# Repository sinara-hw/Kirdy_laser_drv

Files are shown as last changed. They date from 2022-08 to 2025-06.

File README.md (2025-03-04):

# Kirdy

Low Noise Precision Laser Diode Driver with Built-in TEC Temperature Controller  

## Power Input
| Parameter | Min | Typical | Max | Unit | Condition |
| --- | --- | --- | --- | --- | ---|
| Input Voltage | | 12 | | V | |
| Input Current | | | 2 | A|
| PoE Standard | |  PoE+ (802.3at) | | |

Note: TEC Output Current should be limited to ±2A when it is being powered via PoE(802.3af). Otherwise, Kirdy may malfunction.

## Laser Diode Driver
### Current Source Controller  
| Parameter | Min | Typical | Max | Unit | Condition |
| --- | --- | --- | --- | --- | ---| 
| Resolution | | 0.292 | | uA |
| Control Range| | | 307.2 | mA | |
| Current Limit | | 319. | | mA| |
| Compliance voltage | | > 4.928 | | V | |   
| Current Noise (@ 1 kHz) | | < 300 || pA / rt(Hz) | @ DC Bias: 300 mA, Load: 10 Ω Load|
| RMS Noise(10 Hz - 1 MHz) || < 300 | | nA | @ DC Bias: 300 mA, Load: 10 Ω Load| 
| Temperature Coefficient | | ±1 | | ppm/°C | @ DC Bias: 50 mA. Tested Temperature Range: 43-56 °C |

### Photodiode Input
| Parameter | Min | Typical | Max | Unit | Condition |
| --- | --- | --- | --- | --- | ---|
| Photocurrent Range | 0 | | 3.0 | mA | |
| Photocurrent Resolution | | 0.8 | | uA | |
| Bandwidth (-3 dB) | | 500 | | Hz | |

Note1: Circuit may be damaged if photodiode input current exceeds 3.0 mA. User can modify the circuit and reprogram the photodiode current monitor range via the given driver.

Note2: Photodiode operates in photovoaic mode.

### Low Frequency Modulation Input
| Parameter | Min | Typical | Max | Unit | Condition |
| --- | --- | --- | --- | --- | ---|
| Input Voltage | -1.0 | | 1.0 | V | |
| Input Impedance | | 50 or 43.4k | | ohm | Depends on Termination Switch Position |
| Bandwidth (-3 dB) | | 18 | | MHz | @Modulation Depth: 25 mA/V, Input : 1 Vp-p, DC Bias: 150 mA |

Note: Low Frequency Modulation Input can accept DC input to impose a DC offset to the output current.

## TEC Temperature Controller
### TEC Current Output
| Parameter | Min | Typical | Max | Unit | Condition |
| --- | --- | --- | --- | --- | ---|
| Resolution | | 22.9 | | uA | |
| Control Range (Powered via 12 V Barrel Jack) | -3.0 | | 3.0 | A | With Active Cooling |
| Control Range (Powered via PoE(802.3af)) | -2.0 | | 2.0 | A | |
| Compliance Voltage | | 4.3 |  | V | |
| Voltage Reading Resolution | | 3.22 | | mV | |
| Current Reading Resolution | |  2.0 | | mA | |

### TEC Voltage and Current Limit
| Parameter | Min | Typical | Max | Unit | Condition |
| --- | --- | --- | --- | --- | ---|
| Voltage Limit Settable Range| 0 | | 4.3 | V | |
| Voltage Limit Resolution | | 3.14 | | mV | |
| Current Limit Settable Range | -3.0 | | 3.0 | A | |
| Current Limit Resolution | |  1.57 | | mA | |

### NTC Thermistor Sensor
| Parameter | Min | Typical | Max | Unit | Condition |
| --- | --- | --- | --- | --- | ---|
| Resolution | | 0.01 | | mK | With 10 kohm NTC with 3950 B-Constant, 25°C T0 |
| Sampling Rate | | 16.67 | > 1k | Hz | |

Note: Actual Sampling Rate subjects to device operating conditions.

### Digital PID Temperature Controller
| Parameter | Min | Typical | Max | Unit | Condition |
| --- | --- | --- | --- | --- | ---|
| Temperature Stability | | < 1| | mk | Using supplied Kirdy Adapter with its copper plate installed. PID Parameters are obtained from Kirdy Autotune Algorithm. |

Note: Actual Temperature Stability subjects to the ambient environment conditions.

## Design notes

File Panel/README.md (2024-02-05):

# Kirdy Front Panel 

## Front Panel Text Markings
- Font: PrisonGothicPro-Medium.otf
- Drawn in KiCAD 7

## Front Panel Mechanical Design and Drawings
- Drawn in FreeCAD 0.21.2 with a2plus and Exploded Assembly Workbench installed
- Reference Assembly Kit: nVent SCHROFF 20848-668
- Reference drawings: https://git.m-labs.hk/sinara-hw/front-panels/src/branch/master/Kasli_SOC-vNone

## Front Panel Fiber Optic Adapter Mounting Plates
- Drawn in KiCAD 7
- Mounting Plate can be manufactured as 1.5 mm Aluminum Plate or 1.6 mm Single Layer Aluminum PCB
- Possible Fiber Optic Adapter Compatible for Each Type of Mounting Plate
    - Type 1: SC to SC Fibre Optic Adapter
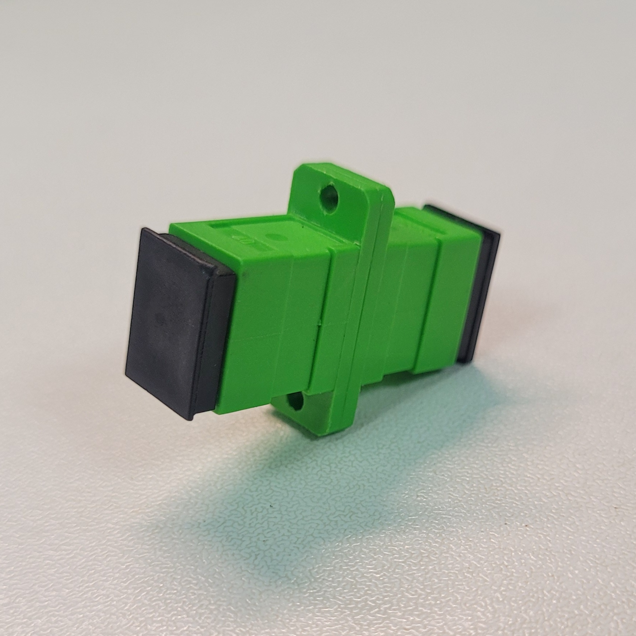
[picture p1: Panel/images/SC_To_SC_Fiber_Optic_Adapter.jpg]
    
    - Type 2: FC to FC Fiber Optic Adapter
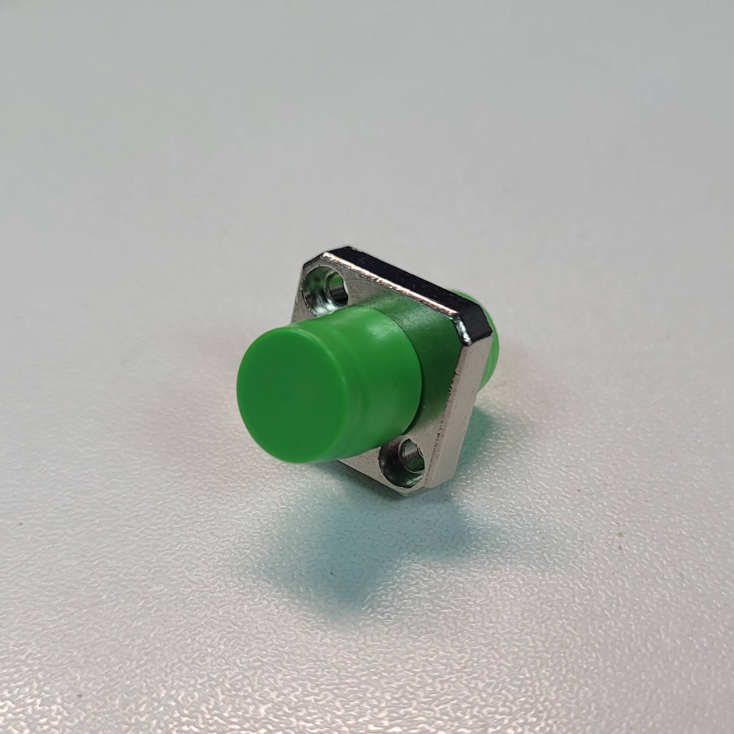
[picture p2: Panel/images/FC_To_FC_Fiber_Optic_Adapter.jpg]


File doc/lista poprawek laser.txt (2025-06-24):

1)add license 0 cerna OHL
2)Add a MOLEX Minifit connector to the board #57
3)Connect 8V LD PWR EN Signal to LD Drive Stage Opamp PD_n
- To all U1, U2, U5 opamp ADA4894-1YRDZ 
4)[Test] Input Power Requirement
- brak reakcji
5) Kirdy HC (High Current) version #54
- brak reakcji 
6) thermoformed plastic laser adapter + fiber holder
- brak reakcji
7)Add Heat Sink to MAX1968 and its Inductors
- 
8) [Test] Evaluation for Maximum Thermostat TEC Output Power
9) generate panel outputs from flake
10) merge flake files
11) 3V3A is unstable if PD Mon Output Stage Voltage is larger than 3.3V
12) move/add protection relay to laser adapter
13) Photodiode Monitor Current Range should be Selectable
14) [TEST] Laser Diode Current Output Temperature Coefficient
15) MAX1968 SHDN Pin is on 5V Voltage Level but it is controlled with 3V3 Voltage Level
16) Mezzanine for second temperature control channel
- nie rozumiem o co im chodzi w tym issiu
17) route relay pins to expansion or laser connector
18) Add a Factory Reset Button for Erasing the settings Stored in Flash
+ rozwiazanie poprzez DFU
19) Add a Switch to the Front Panel for User to Select Whether Kirdy By default Power On Laser Diode and TEC
- nie wiem czy to ma sens
20) Add a 3 Pin Header for Configuring the Photodiode to Operate in Photovoltaic or Photoconductive mode

21) Confusing LD-, LD+, PD- and PD+ Net Name and Markings
- poprawione
22) Lacking EEPROM Preprogrammed with Unique Mac Address
- dodałem pamieci 24AA02E48T-I/OT do STM32 
23) LD overcurrent with all modulation switches are OFF
- nie wiem co z tym zrobic, albo dodac kolejny dzielnik albo moze potencjometr cyfrowy, ale popsuje to szumy
24) Ethernet link drops temporarily when +8V comes on
- faktycznie problem moze istniec, ale autor issiu nie podał powodu i sposobu naprawy
25) PoE unstable power-up
- tu problem jest po stornie switch z POE nie płytki
26) MCU's Firmware Starts before Analog Power Rails are "Power Good"
- dodałem rezystory 10k i linie PG podłaczyłem w wszystkich LDO

wejscie POE/JACK +12V
zaislane z +12V -> 5V
zasilane z +12V -> +3.3V

zasilanie z +12V
+9V 1.5A
+9VA 200mA
+8V
+5VA
zasilane z +5VA  ->   +3.3VA

zasilanie +9V CP
zasilane z -9V   ->   -6V 
+15V

27) Fiber optic adapter mounted on front panel may block the access of alternate programming pin header
+ 28) components bump into card guides
- poprawione, zostały dodane marginesy po 2.5mm z kazdej strony
29) [TEST] LD Driver Current Noise

moje zmiany 
zmiana szerokosci sciezek na 6-8 mil
przelotki zmiana na 0.3/0.6 mm
zmiana layer stack na JLC04161H-3313

- pomiar prądu 
- rozne konfiguracje laser 
+ umascienie katody 
- ba slepo pomiar pradu diody /moc
czy sa kunary ?

TEC - dlaczego niski prad
- ddoac zabzpiecznie na pinach IO
dodać zabezpiczenie do diody laserowej

tylko jeden scalak na BOT !!!!! U3 U6

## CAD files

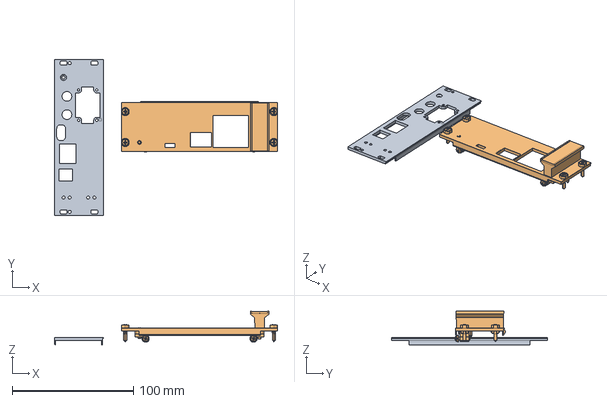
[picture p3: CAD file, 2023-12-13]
Panel/kirdy_front_panel.asm.FCStd
183.7 x 128.4 x 27.8 mm
kirdy_front_panel1_001
Kasli-SOC_Panel1_001

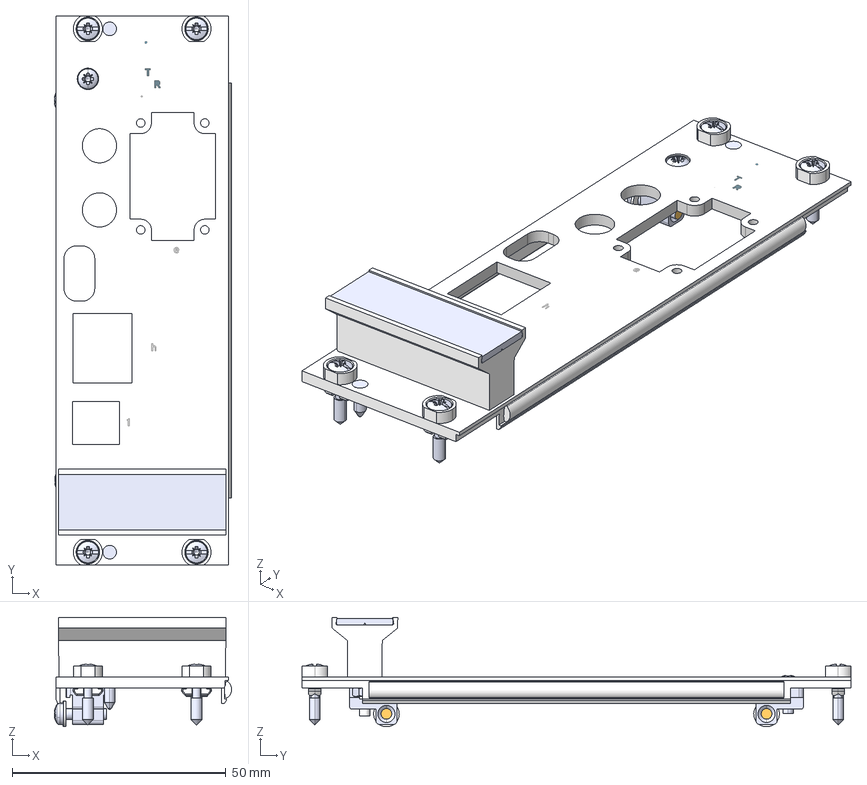
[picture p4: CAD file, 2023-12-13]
Panel/output/FP_1550_3U8HP_PANEL_Mechanical_Drawings_Rev_A/FP_1550_3U8HP_PANEL.step
41.4 x 128.4 x 25.6 mm
FP_1550_3U8HP_CUTOUT_001
SLEEVE GREY PLAS. M2.5 BL
SLEEVE GREY PLAS. M2.5 TL
SLEEVE GREY PLAS. M2.5 TR
SLEEVE GREY PLAS. M2.5 BR
SCREW COLLAR M2.5X12.3 BL
SCREW COLLAR M2.5X12.3 BR
SCREW COLLAR M2.5X12.3 TL
SCREW COLLAR M2.5X12.3 TR
SCR M2.5*8 OVL PHL ST NI
WASHER PLN.M2.7 DIN125 B
SCR M2.5*6 PAN PHL NI DIN7985 B
FP-ALIGNMENT PIN (LOCALIZATION) T
FP-ALIGNMENT PIN (LOCALIZATION) B
EMC GASKET FABRIC 3U

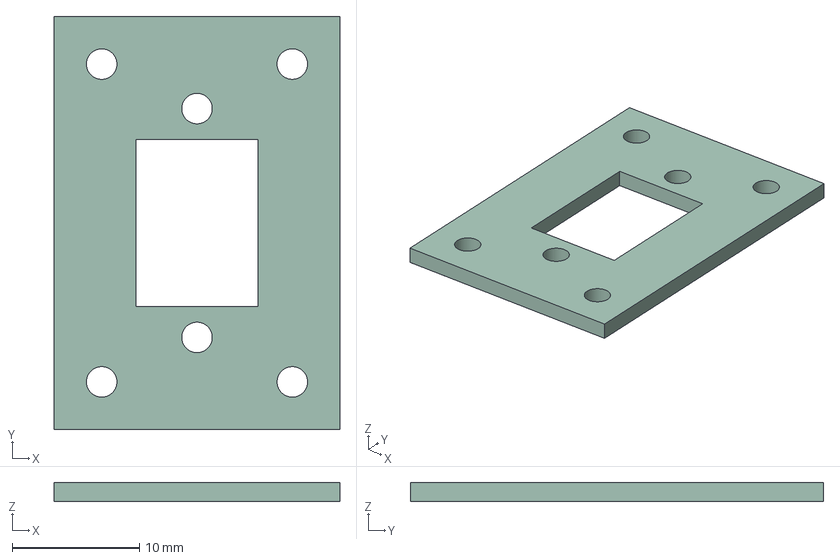
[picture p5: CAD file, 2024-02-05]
Panel/output/FP_1550_Fiber_Optic_Adapter_Mounting_Plate_Type_1/FP_1550_Fiber_Optic_Adapter_Mounting_Plate_Type_1_r0_1rc1.step
22.5 x 32.5 x 1.50 mm

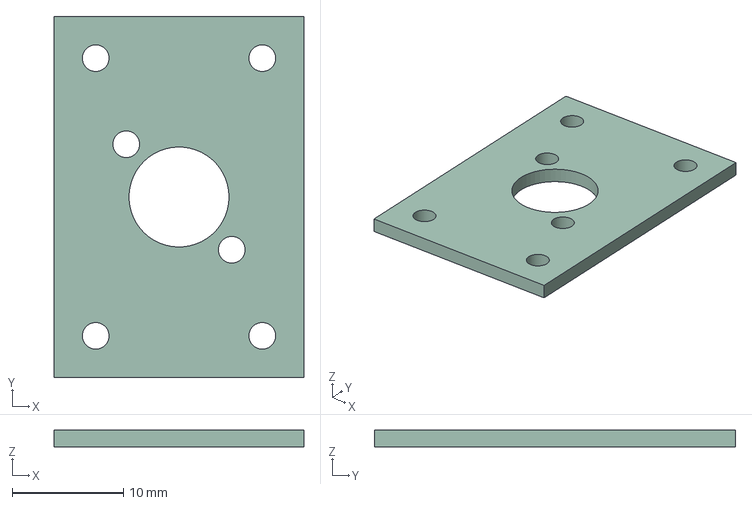
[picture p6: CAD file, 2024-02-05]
Panel/output/FP_1550_Fiber_Optic_Adapter_Mounting_Plate_Type_2/FP_1550_Fiber_Optic_Adapter_Mounting_Plate_Type_2_r0_1rc1.step
22.5 x 32.5 x 1.50 mm

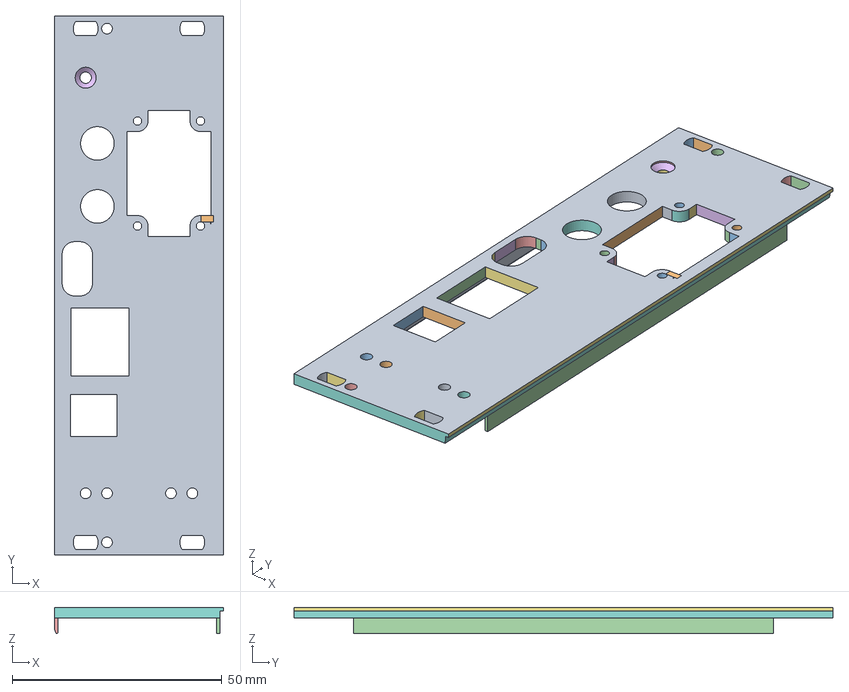
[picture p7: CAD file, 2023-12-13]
Panel/kirdy_front_panel.FCStd
40.3 x 128.4 x 6.20 mm

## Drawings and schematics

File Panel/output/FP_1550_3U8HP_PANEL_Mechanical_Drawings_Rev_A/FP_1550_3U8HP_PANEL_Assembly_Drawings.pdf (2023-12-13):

5 3 4

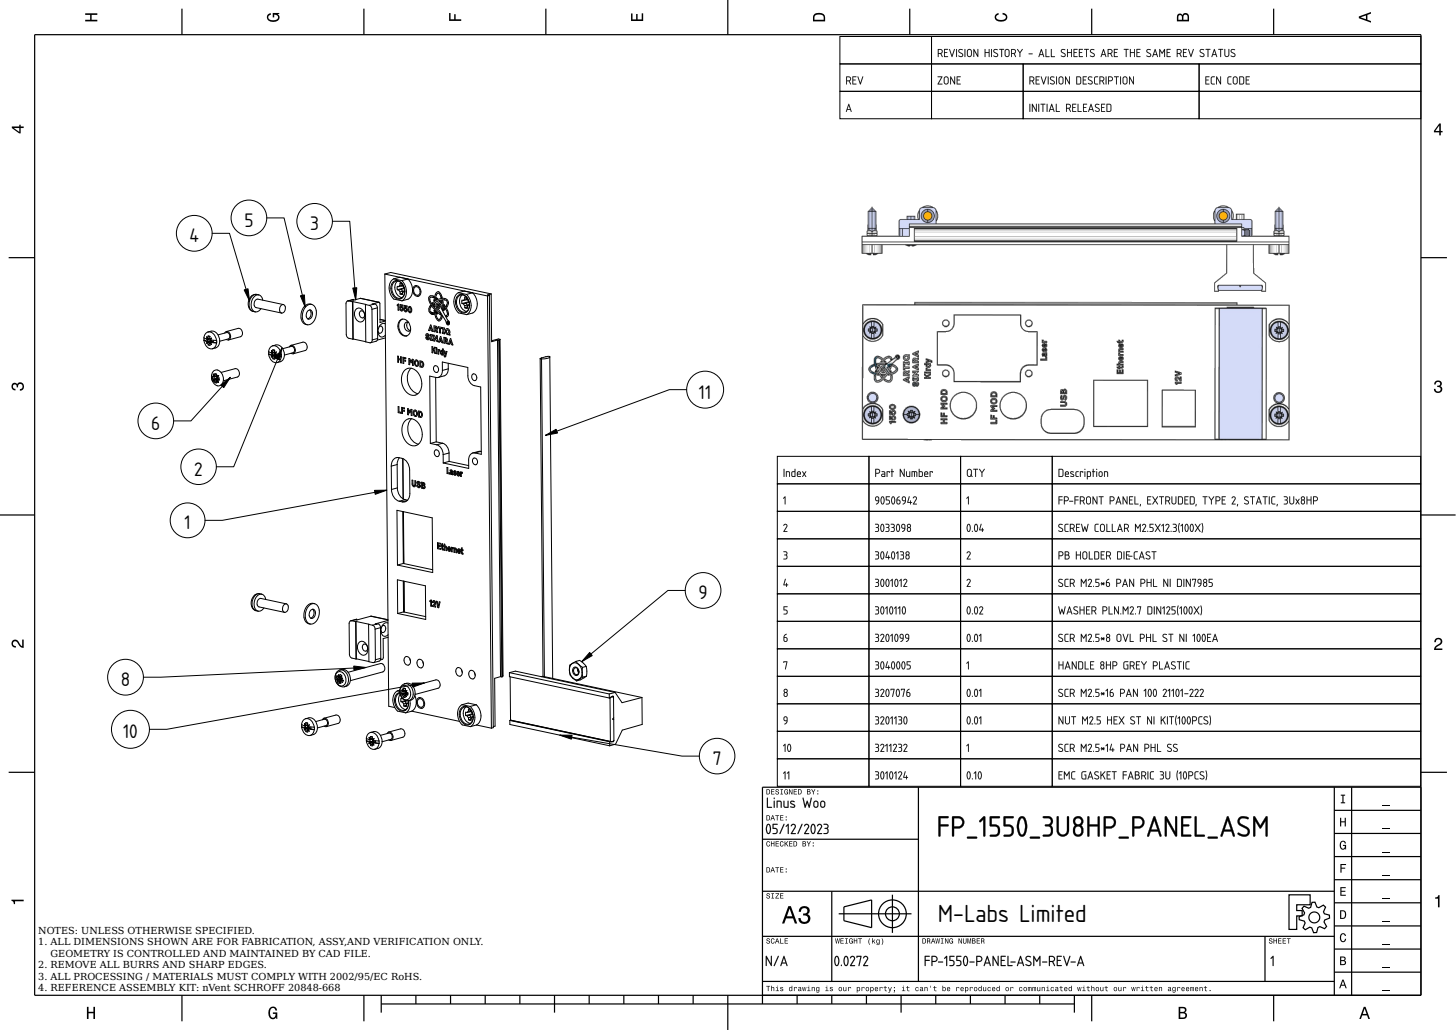
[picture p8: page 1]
M-Labs Limited

NOTES: UNLESS OTHERWISE SPECIFIED. 1. ALL DIMENSIONS SHOWN ARE FOR FABRICATION, ASSY,AND VERIFICATION ONLY. GEOMETRY IS CONTROLLED AND MAINTAINED BY CAD FILE. 2. REMOVE ALL BURRS AND SHARP EDGES. 3. ALL PROCESSING / MATERIALS MUST COMPLY WITH 2002/95/EC RoHS. 4. REFERENCE ASSEMBLY KIT: nVent SCHROFF 20848-668

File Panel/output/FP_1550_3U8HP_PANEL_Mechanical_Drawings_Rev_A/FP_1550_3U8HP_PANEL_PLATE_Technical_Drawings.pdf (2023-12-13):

4

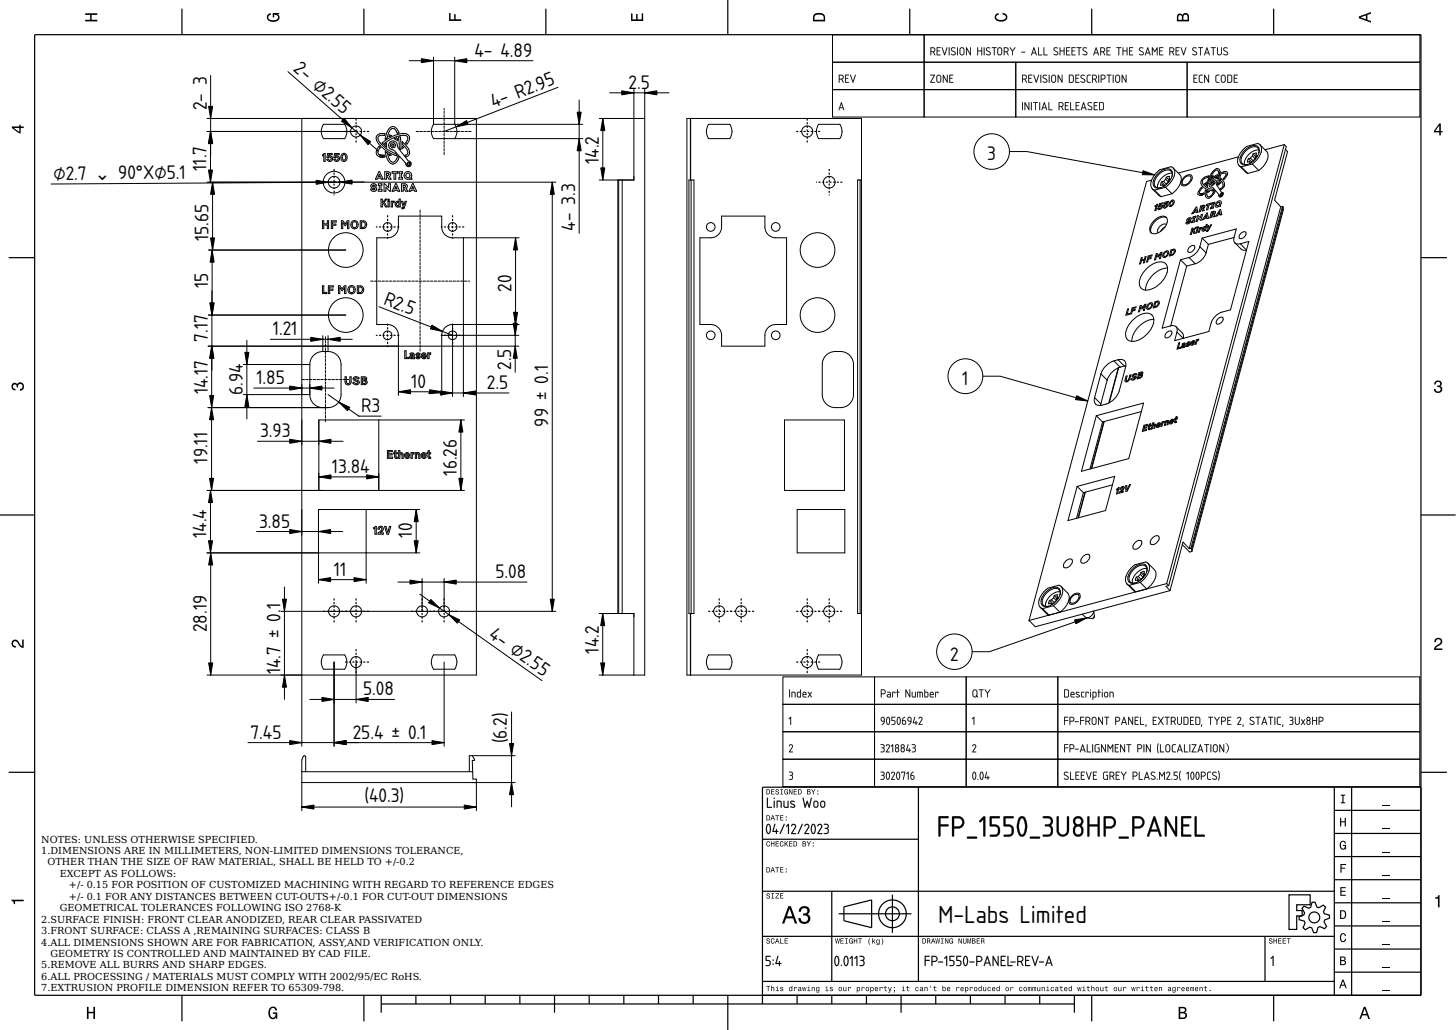
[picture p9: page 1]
2 1 3 M-Lab; Limite; RWIS; CIFIE; N-LIMIT; DIM; SIO; DIS; RIC; WIN; FINIS; DIZ; SIVAT; AININ; ATIO; RIFIC

D. 1.DIMENSIONS ARE IN MILLIMETERS, NO
E, OTHER THAN THE SIZE OF RAW MATERIAL, SHALL BE HELD TO +/-0.2 EXCEPT AS FOLLOWS: +/- 0.15 FOR POSITION OF CUSTOMIZED MACHINING WITH REGARD TO RE

LY. GEOMETRY IS CONTROLLED AND MAINTAINED BY CAD FILE. 5.REMOVE ALL BURRS AND SHARP EDGES. 6.ALL PROCESSING / MATERIALS MUST COMPLY WITH 2002/95/EC RoHS. 7.EXTRUSION PROFILE DIMENSION REFER TO 65309-798.

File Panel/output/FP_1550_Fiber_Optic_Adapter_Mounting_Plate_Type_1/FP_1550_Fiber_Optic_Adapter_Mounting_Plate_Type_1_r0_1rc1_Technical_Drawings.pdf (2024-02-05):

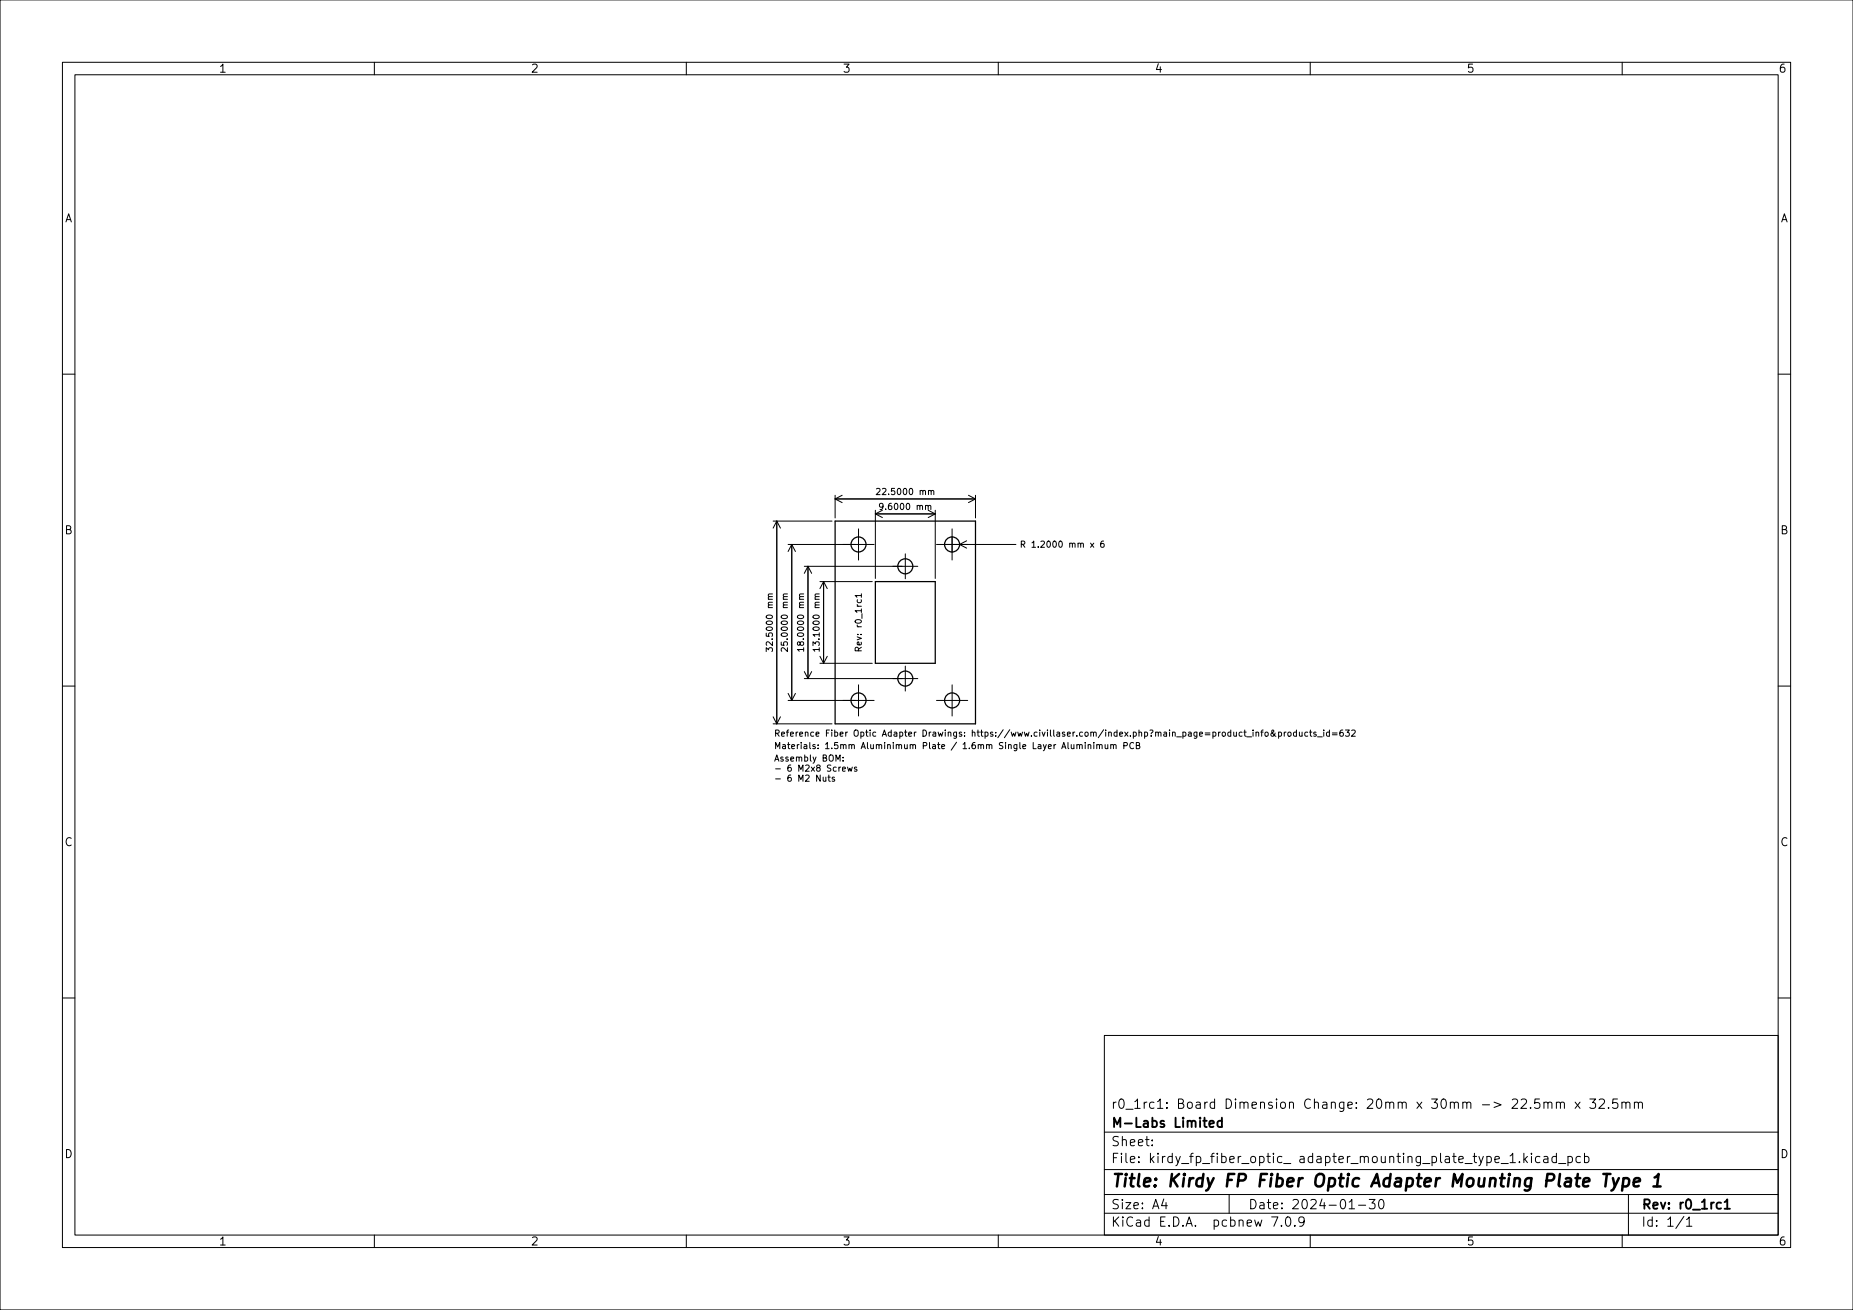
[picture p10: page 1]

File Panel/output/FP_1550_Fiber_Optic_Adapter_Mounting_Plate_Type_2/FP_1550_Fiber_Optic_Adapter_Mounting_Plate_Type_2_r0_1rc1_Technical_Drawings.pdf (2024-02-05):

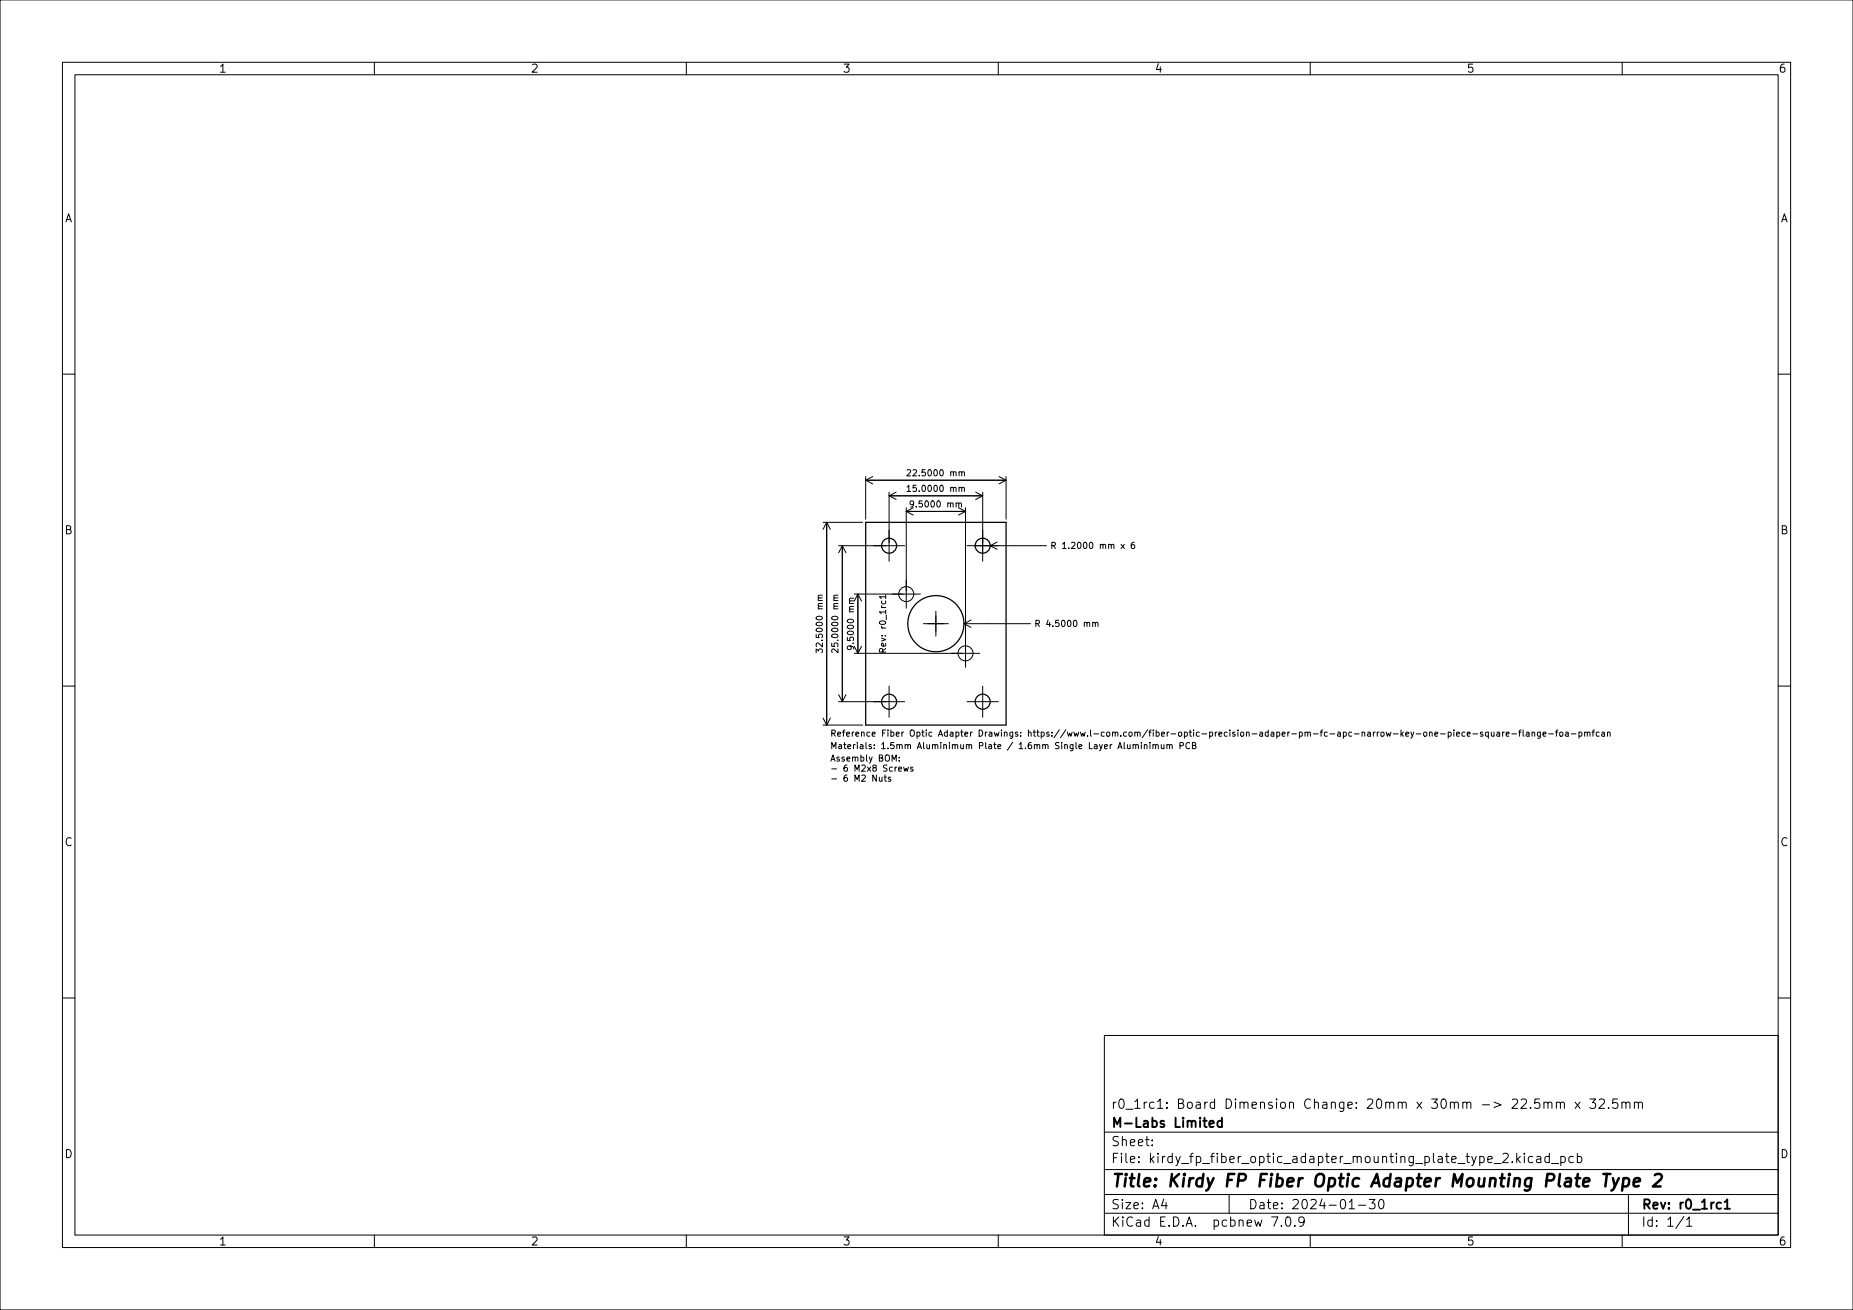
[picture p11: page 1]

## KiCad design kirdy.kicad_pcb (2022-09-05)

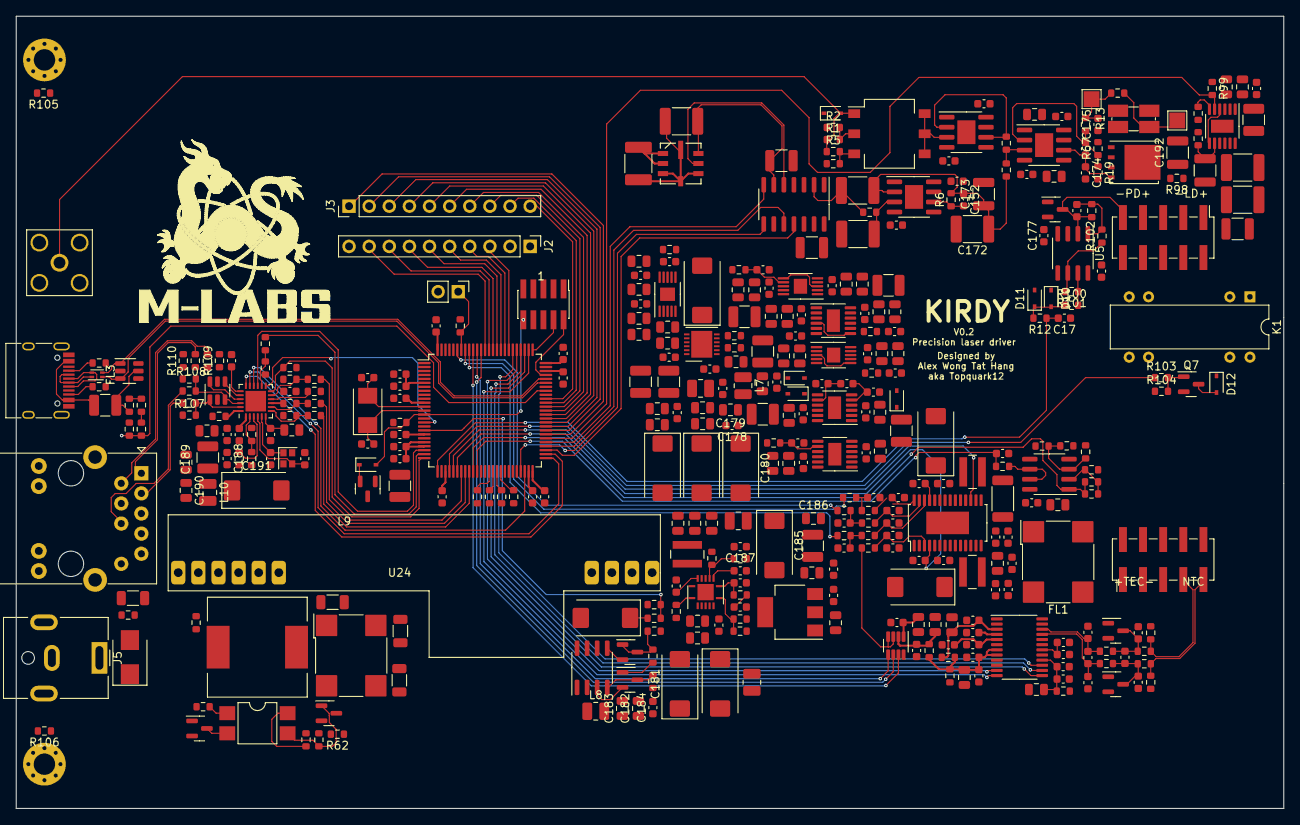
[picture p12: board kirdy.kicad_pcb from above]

Board: 4 copper layers, 160.0 x 100.0 mm, 390 parts (0 on the bottom side), 224 nets.

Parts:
C1, C5, C6: 2u PET; C_1812_4532Metric
C2, C84, C91, C172: 10u PP; C_1812_4532Metric
C3, C4, C70, C77, C173, C192: 100n PPS; C_1210_3225Metric
C7, C8, C9, C10, C11, C12, C14, C17, C23, C24, C25, C26, C27, C28, C30, C31, C35, C36, C41, C46, C47, C62, C63, C64, C65, C66, C67, C68, C69, C71, C72, C73, C74, C75, C76, C78, C79, C80, C81, C98, C99, C102, C103, C104, C105, C106, C107, C108, C109, C111, C112, C114, C115, C116, C117, C118, C119, C123, C127, C133, C138, C139, C140, C144, C149, C159, C160, C164, C166, C167, C169, C170, C176, C177, C178, C184, C187, C188: 100n; C_0603_1608Metric
C13, C122, C124, C125, C132, C134: 10n; C_0603_1608Metric
C15, C16, C33, C34, C37, C39, C44, C45, C48, C49, C50, C51, C52, C53, C54, C55, C56, C57, C58, C59, C60, C61, C82, C83, C85, C86, C87, C88, C90, C92, C93, C94, C95, C96, C97, C100, C101, C113, C126, C136, C142, C143, C153, C154, C156, C158, C161, C165, C168, C179, C182, C183, C186, C189, C190: 10u; C_0805_2012Metric
C18, C19, C20, C29: 2u2; C_0603_1608Metric
C21, C22: 12p; C_0603_1608Metric
C32, C40, C89, C131, C141, C155, C157, C180, C181, C185, C191: 220u; CP_EIA-7343-15_Kemet-W
C38, C42, C43, C110, C120, C121, C128, C129, C130, C135, C137: 1u; C_0603_1608Metric
C145, C146, C148: 4n7; C_1206_3216Metric
C147, C152: 1n6; C_0603_1608Metric
C150: 22n; C_0603_1608Metric
C151: 39p; C_0603_1608Metric
C162, C163: 18p; C_0603_1608Metric
C171: DNP; C_1206_3216Metric
C174, C175: DNP; C_0603_1608Metric
D1: AQ4020-01FTG-C; D_SOD-323
D2, D7, D8: BAV199; SOT-23
D3, D4, D5, D6, D10, D11, D12: B5819; D_SOD-323
D9: SMBJ13A-13-F; D_SMB
FB1, FB2, FB3, FB4, FB5, FB6, FB7, FB8, FB9, FB10, FB11, FB12: 1K@100MHz; L_1210_3225Metric
FL1, FL2: 2x1m; L_CommonModeChoke_Wuerth_WE-SL5
FL3: 90R@100MHz; L_CommonModeChoke_Coilcraft_0603USB
H1, H2: MountingHole_Pad; MountingHole_2.7mm_M2.5_Pad_Via
J1: MOD_IN; SMA_Amphenol_132203-12_Horizontal
J2, J3: Conn_01x10; PinHeader_1x10_P2.54mm_Vertical
J4: Conn_02x05_Odd_Even; PinHeader_2x05_P1.27mm_Vertical_SMD
J5: Barrel_Jack; BarrelJack_CUI_PJ-063AH_Horizontal
J6: RJ45_Abracon_ARJP11A-MASA-B-A-EMU2; RJ45_Abracon_ARJP11A-MA_Horizontal
J7: USB_C_Receptacle_USB2.0; USB_C_Receptacle_HRO_TYPE-C-31-M-12
J8, J9: Conn_02x05_Odd_Even; PinHeader_2x05_P2.54mm_Vertical_SMD
JP1: DNP; PinHeader_1x02_P2.54mm_Vertical
K1: DIP12-1C90-51L; Relay_StandexMeder_DIP_LowProfile
L1, L4, L7, L8, L9, L10: 1u; L_1008_2520Metric
L2, L3: 6.8u; L_Wuerth_MAPI-4030
L5: 10u; L_Wuerth_WE-PD-Typ-LS
L6: 3u3; L_Wuerth_MAPI-4020
Q1: SQJA70EP-T1; TDSON-8-1
Q2, Q3, Q7: BSS138; SOT-23
Q4, Q6: BC857; SOT-23
Q5: AOSP21321; SOIC-8_3.9x4.9mm_P1.27mm
R1: 90; R_0603_1608Metric
R2, R62: 10; R_0603_1608Metric
R3, R104: 2k; R_0603_1608Metric
R4: 1; R_0603_1608Metric
R5: 99; R_0603_1608Metric
R6, R8, R10, R103, R107, R108, R109, R110: 100; R_0603_1608Metric
R7: 300; R_0603_1608Metric
R9, R12, R100, R101, R102: 1k; R_0603_1608Metric
R11, R91, R105, R106: 0; R_0603_1608Metric
R13: 10; R_Shunt_VCS1625ZP
R14, R15, R16, R17, R20, R21, R33, R34, R35, R36, R37, R38, R46, R47, R48, R49, R66, R69, R77, R78, R79, R81, R82, R83, R95, R96, R97: 10k; R_0603_1608Metric
R19, R67: DNP; R_0603_1608Metric
R22: 60k4; R_0603_1608Metric
R23: 9k09; R_0603_1608Metric
R24: 470; R_0603_1608Metric
R25: 80k6; R_0603_1608Metric
R26, R99: 51k; R_0603_1608Metric
R27, R29, R61, R68, R70: 33k2; R_0603_1608Metric
R28, R30: 150k; R_0603_1608Metric
R31, R32, R39, R40, R73, R74, R75, R76, R85, R86, R87, R88: 33; R_0603_1608Metric
R41, R42, R80: 1k6; R_0603_1608Metric
R43, R44, R50, R51: 51; R_0603_1608Metric
R45: 50m; R_2010_5025Metric
R52, R53, R58: 20k; R_0603_1608Metric
R54, R55: 5k11 5ppm; R_0603_1608Metric
R56, R89, R90: 220; R_0603_1608Metric
R57, R59, R60, R63, R72: 82k; R_0603_1608Metric
R64: 4k12; R_0603_1608Metric
R65: 52k3; R_0603_1608Metric
R71: 1k3; R_0603_1608Metric
R84: 12k1; R_0603_1608Metric
R92, R93, R94: 5k1; R_0603_1608Metric
R98: 3.3; R_0603_1608Metric
SW1: SW_DIP_x03; SW_DIP_SPSTx03_Slide_Omron_A6S-310x_W8.9mm_P2.54mm
TP9, TP10: TestPoint; TestPoint_Pad_2.0x2.0mm
U1: LTC6655BHLS8-4.096; LCC127P500X500X155-8N
U2: MAX5719xSD; SOIC-14_3.9x8.7mm_P1.27mm
U3, U4, U6: ADA4898-1YRDZ; SOIC-8-1EP_3.9x4.9mm_P1.27mm_EP2.29x3mm
U5: LM358; SOIC-8_3.9x4.9mm_P1.27mm
U7: STM32F407VGTx; LQFP-100_14x14mm_P0.5mm
U8: STM809SWX6F; SOT-23
U9: LTC3261; MSOP-12-1EP_3x4mm_P0.65mm_EP1.65x2.85mm
U10: LT3081xDF; DFN-12-1EP_4x4mm_P0.5mm_EP2.66x3.38mm
U11, U14, U16: LT3042xMSE; MSOP-10-1EP_3x3mm_P0.5mm_EP1.68x1.88mm
U12, U13: LT3045xMSE; MSOP-12-1EP_3x4mm_P0.65mm_EP1.65x2.85mm
U15: LT3094xMSE; MSOP-12-1EP_3x4mm_P0.65mm_EP1.65x2.85mm
U17: AD5680; SOT-23-8
U18: AD7172-2; TSSOP-24_4.4x7.8mm_P0.65mm
U19: RS8552; SOIC-8_3.9x4.9mm_P1.27mm
U20: MAX1968xUI; HTSSOP-28-1EP_4.4x9.7mm_P0.65mm_EP2.85x5.4mm
U21: ACPL-217-500E; SMDIP-4_W7.62mm
U22: TPS54620; Texas_S-PVQFN-N14
U24: PM1202
U25: AMS1117-3.3; SOT-223-3_TabPin2
U26: LAN8742A; QFN-24-1EP_4x4mm_P0.5mm_EP2.6x2.6mm
U27, U28: USBLC6-4SC6; SOT-23-6
Y1: 8MHz; Crystal_SMD_5032-2Pin_5.0x3.2mm
Y2: 25MHz; Crystal_SMD_2016-4Pin_2.0x1.6mm

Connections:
+3.3VA: C79.1, C86.1, C93.1, C126.1, C127.1, D2.2 (A), D7.2 (A), D8.2 (A), D10.1 (K), J8.7, R39.2, R40.2, R47.1, U14.9 (OUTS), U14.10 (OUT), U19.8 (V+)
+3V3: C20.1, C23.1, C24.1, C25.1, C26.1, C27.1, C30.1, C31.1, C160.1, C161.1, C166.1, FB1.1, J2.2, J4.1, JP1.2 (B), L10.2, R14.1, R15.1, R16.1, R17.1, R21.1, R56.1, R77.2, R78.2, R79.2, R80.2, R81.2, U7.6 (VBAT), U7.11 (VDD), U7.19 (VDD), U7.28 (VDD), U7.50 (VDD), U7.75 (VDD), U7.100 (VDD), U8.3 (VCC), U25.2 (VO), U26.9 (VDDIO)
+5V: C128.1, C129.1, C130.1, C131.1, C153.1, C154.1, C156.1, C157.1, L6.2, L9.1, R65.2, U20.1 (VDD), U20.9 (PVDD2), U20.11 (PVDD2), U20.18 (PVDD1), U20.20 (PVDD1)
+5VA: C1.1, C4.1, C78.1, C85.1, C92.1, C113.1, C114.1, FB7.1, U1.1 (~SHDN), U1.2 (VIN), U2.14 (VDD), U13.10 (OUTS), U13.11 (OUT), U13.12 (OUT), U17.1 (VDD)
+8V: C77.1, C84.1, C91.1, J8.1, K1.1, U12.10 (OUTS), U12.11 (OUT), U12.12 (OUT)
+9V: C75.1, C82.1, C89.1, FB5.1, FB6.1, L7.1, U10.1 (OUT), U10.2 (OUT), U10.3 (OUT), U10.4 (OUT), U10.7 (IMON), U10.8 (TEMP), U10.13 (OUT)
+9VA: C7.1, C8.1, C76.1, C83.1, C90.1, C176.2, U3.7 (V+), U3.8 (~PD), U4.7 (V+), U4.8 (~PD), U5.8 (V+), U11.9 (OUTS), U11.10 (OUT)
+12V: C32.1, C33.1, C34.1, C36.1, C181.1, C182.1, C183.1, C184.1, D12.1 (K), K1.6, L1.1, L4.1, L8.2
+15V: C11.1, C15.1, C81.1, C88.1, C95.1, U6.7 (V+), U6.8 (~PD), U16.9 (OUTS), U16.10 (OUT)
-6V: C9.2, C10.2, C12.2, C16.2, C80.1, C87.1, C94.1, C177.2, U3.4 (V-), U3.9 (EP), U4.4 (V-), U4.9 (EP), U5.4 (V-), U6.4 (V-), U6.9 (EP), U15.10 (OUTS), U15.11 (OUT), U15.12 (OUT)
-9V: C47.1, C48.1, D6.1 (K), FB9.1, U9.4 (VOUT)
/Ehternet/AVDDT_PHY: C167.1, C168.1, C169.1, C170.1, FB11.1, J6.4 (CT), J6.5 (CT), U26.1 (VDD2A), U26.19 (VDD1A), U27.5 (VBUS)
/Ehternet/ETH_LED_1: R83.1, R90.1, U26.2 (LED2)
/Ehternet/ETH_LED_2: R89.1, U26.3 (LED1)
/Ehternet/ETH_SHIELD: C171.1, J6.7, J6.15 (SHIELD), R91.1
/Ehternet/PHY_NRST: U7.23 (PA0), U26.15 (nRST)
/Ehternet/PHY_RD_N: R85.1, R108.2, U26.22 (RXN), U27.3 (I/O2)
/Ehternet/PHY_RD_P: R86.1, R107.2, U26.23 (RXP), U27.1 (I/O1)
/Ehternet/PHY_TD_N: R87.1, R109.1, U26.20 (TXN), U27.4 (I/O3)
/Ehternet/PHY_TD_P: R88.1, R110.1, U26.21 (TXP), U27.6 (I/O4)
/Ehternet/POE_VC+: J6.9 (V+), L5.1, R57.1
/Ehternet/POE_VC-: J6.10 (V-), Q3.2 (S), R58.2, R59.2, R62.2
/Ehternet/RMII_CRS_DV: R75.1, U7.32 (PA7)
/Ehternet/RMII_MDC: U7.16 (PC1), U26.13 (MDC)
/Ehternet/RMII_MDIO: R80.1, U7.25 (PA2), U26.12 (MDIO)
/Ehternet/RMII_REF_CLK: R76.1, U7.24 (PA1)
/Ehternet/RMII_RXD0: R73.1, U7.33 (PC4)
/Ehternet/RMII_RXD1: R74.1, U7.34 (PC5)
/Ehternet/RMII_TXD0: U7.51 (PB12), U26.17 (TXD0)
/Ehternet/RMII_TXD1: U7.52 (PB13), U26.18 (TXD1)
/Ehternet/RMII_TX_EN: U7.48 (PB11), U26.16 (TXEN)
/MCU/LDAC_CLK: U2.8 (SCLK), U7.47 (PB10)
/MCU/LDAC_CS: U2.7 (~CS), U7.55 (PD8)
/MCU/LDAC_LOAD: U2.11 (~LDAC), U7.53 (PB14)
/MCU/LDAC_MOSI: U2.10 (DIN), U7.54 (PB15)
/MCU/LD_EN: R99.2, U7.56 (PD9), U12.5 (PG)
/MCU/MCU_RSTn: D3.1 (K), Q2.1 (G), U8.2 (RST)
/MCU/PD_MON: C17.2, R12.1, U7.26 (PA3)
/MCU/POE_PWR_SRC: R68.2, R69.1, U7.18 (PC3)
/MCU/PWM_MAXIN: R35.1, U7.92 (PB6)
/MCU/PWM_MAXIP: R34.1, U7.95 (PB8)
/MCU/PWM_MAXV: R33.1, U7.93 (PB7)
/MCU/RST: D3.2 (A), J4.10, R21.2, U7.14 (NRST)
/MCU/SWCLK: J4.4, U7.76 (PA14)
/MCU/SWDIO: J4.2, U7.72 (PA13)
/MCU/TADC_CLK: U7.78 (PC10), U18.13 (SCLK)
/MCU/TADC_CS: U7.77 (PA15), U18.12 (DIN)
/MCU/TADC_MISO: U7.79 (PC11), U18.14 (~CS)
/MCU/TADC_MOSI: U7.80 (PC12), U18.11 (DOUT/~RDY)
/MCU/TADC_SYNC: U7.81 (PD0), U18.15 (~SYNC/~ERR)
/MCU/TDAC_CLK: U7.89 (PB3), U17.6 (SCLK)
/MCU/TDAC_MOSI: U7.91 (PB5), U17.7 (DIN)
/MCU/TDAC_SYNC: U7.90 (PB4), U17.5 (~SYNC)
/MCU/TEC_ISEN: C118.1, R42.1, U7.36 (PB1)
/MCU/TEC_SHDN: U7.30 (PA5), U20.17 (~SHDN)
/MCU/TEC_VREF: C120.1, U7.31 (PA6), U20.4 (REF)
/MCU/TEC_VSEN: R48.1, R49.1, U7.35 (PB0), U19.1
/MCU/USB_DN: FL3.2, U7.70 (PA11), U28.3 (I/O2)
/MCU/USB_DP: FL3.3, U7.71 (PA12), U28.1 (I/O1)
/MCU/USB_VBUS: R96.1, R97.2, U7.68 (PA9)
/MCU/VREF: C28.1, C29.1, FB1.2, U7.21 (VREF+), U7.22 (VDDA)
/MCU/~LD_SHORT: R103.1, U7.29 (PA4)
/driveStage/LD-: J8.3, K1.7, K1.8, Q1.5 (D), R98.2
/driveStage/PD_A: C14.2, D2.3 (K), J8.9, R9.2, U5.2 (-)
/thermostat/ADC_A3V3: C100.1, C105.1, C116.1, R31.2, R32.2, R39.1, U18.7 (AVDD1), U18.8 (AVDD2)
/thermostat/ADC_D3V3: C101.1, C106.1, C112.1, R40.1, U18.16 (IOVDD)
/thermostat/ADC_REF: C97.1, C99.1, R32.1, R54.1, U18.3 (REF+)
/thermostat/DAC_REF: C96.1, C98.1, R31.1, U17.2 (VREF)
/thermostat/MAXIN: C109.1, R38.2, U20.26 (MAXIN)
/thermostat/MAXIP: C108.1, R37.2, U20.27 (MAXIP)
/thermostat/MAXV: C107.1, R36.2, U20.28 (MAXV)
/thermostat/NTC+: J9.9, R50.2, R54.2
/thermostat/NTC-: J9.7, R51.2, R55.1
/thermostat/TEC+: FL1.4, J9.1
/thermostat/TEC-: FL1.3, J9.3
GND: C1.2, C2.1, C3.1, C4.2, C6.2, C7.2, C8.2, C9.1, C10.1, C11.2, C12.1, C15.2, C16.1, C17.1, C18.2, C19.2, C20.2, C21.1, C22.2, C23.2, C24.2, C25.2, C26.2, C27.2, C28.2, C29.2, C30.2, C31.2, C32.2, C33.2, C34.2, C35.2, C36.2, C37.1, C39.2, C40.2, C41.1, C44.2, C45.2, C46.2, C47.2, C48.2, C49.2, C50.2, C51.2, C52.2, C53.2, C54.2, C55.2, C56.2, C57.2, C58.2, C59.2, C60.2, C61.2, C62.2, C63.2, C64.2, C65.2, C66.2, C67.2, C68.2, C69.2, C70.2, C71.2, C72.2, C73.2, C74.2, C75.2, C76.2, C77.2, C78.2, C79.2, C80.2, C81.2, C82.2, C83.2, C84.2, C85.2, C86.2, C87.2, C88.2, C89.2, C90.2, C91.2, C92.2, C93.2, C94.2, C95.2, C96.2, C97.2, C98.2, C99.2, C100.2, C101.2, C102.2, C103.2, C104.2, C105.2, C106.2, C107.2, C108.2, C109.2, C110.2, C111.2, C112.2, C113.2, C114.2, C115.2, C116.2, C117.2, C118.2, C119.2, C120.2, C121.2, C122.1, C124.2, C125.2, C126.2, C127.2, C128.2, C129.2, C130.2, C131.2, C132.1, C134.2, C135.1, C137.2, C138.1, C140.2, C141.2, C142.2, C143.2, C144.2, C146.2, C147.2, C148.2, C150.2, C151.2, C153.2, C154.2, C155.2, C156.2, C157.2, C158.2, C159.2, C160.2, C161.2, C162.1, C163.1, C164.2, C165.2, C166.2, C167.2, C168.2, C169.2, C170.2, C171.2, C172.2, C173.2, C176.1, C177.1, C178.2, C179.2, C180.2, C181.2, C182.2, C183.2, C184.2, C185.2, C186.2, C187.2, C188.2, C189.2, C190.2, C191.2, C192.2, D1.1 (A1), D2.1 (K), D7.1 (K), D8.1 (K), D9.2 (A2), D11.2 (A), J1.2 (Ext), J2.1, J2.10, J4.3, J4.5, J5.2, J6.12 (LLED-), J6.14 (RLED-), J7.A1 (GND), J7.A12 (GND), J7.B1 (GND), J7.B12 (GND), J7.S1 (SHIELD), J8.2, J8.4, J8.5, J8.6, J8.8, J8.10, J9.2, J9.4, J9.5, J9.6, J9.8, J9.10, Q2.2 (S), Q7.2 (S), R2.1, R4.1, R13.3, R13.4, R20.1, R22.2, R23.1, R24.1, R25.1, R26.1, R27.1, R28.1, R29.1, R46.1, R55.2, R61.2, R63.2, R66.2, R69.2, R70.2, R72.2, R82.1, R83.2, R84.2, R91.2, R92.2, R93.2, R97.1, R99.1, R104.1, R105.1, R106.1, R107.1, R108.1, R109.2, R110.2, U1.3 (GND), U1.4 (GND), U1.5 (GND), U1.8 (GND), U2.3 (AGNDF), U2.4 (AGNDS), U2.12 (DGND), U5.3 (+), U5.5 (+), U7.10 (VSS), U7.20 (VSSA), U7.27 (VSS), U7.74 (VSS), U7.99 (VSS), U8.1 (VSS), U9.2 (RT), U9.11 (MODE), U9.13 (GND), U11.5 (ILIM), U11.8 (GND), U11.11 (GND), U12.9 (GND), U12.13 (GND), U13.6 (ILIM), U13.9 (GND), U13.13 (GND), U14.5 (ILIM), U14.8 (GND), U14.11 (GND), U15.6 (ILIM), U15.9 (GND), U16.5 (ILIM), U16.8 (GND), U16.11 (GND), U17.8 (GND), U18.1 (AIN4), U18.2 (REF-), U18.6 (AVSS), U18.17 (DGND), U18.23 (AIN2), U18.24 (AIN3), U19.4 (V-), U20.2 (GND), U20.5 (PGND), U20.7 (PGND), U20.12 (FREQ), U20.22 (PGND), U20.24 (PGND), U20.29 (GND), U22.2 (GND), U22.3 (GND), U22.15 (EP), U24.7 (-VDC), U24.8 (-VDC), U25.1 (GND), U26.25 (EP), U27.2 (GND), U28.2 (GND), Y2.2, Y2.4
IN: C49.1, C56.1, C63.1, FB3.2, U10.9 (IN), U10.10 (IN), U10.11 (IN), U10.12 (IN)
unnamed: C2.2, C3.2, U1.7 (VOUT_F), U2.6 (REFF)
unnamed: C5.1, R3.1, U2.2 (OUT)
unnamed: C6.1, R3.2, U4.3 (+)
unnamed: C13.1, C174.1, Q1.4 (G), U6.6
unnamed: C13.2, R10.1, R19.1, R67.1, U6.2 (-)
unnamed: C14.1, R9.1, R102.2, U5.1
unnamed: C18.1, U7.49 (VCAP_1)
unnamed: C19.1, U7.73 (VCAP_2)
unnamed: C21.2, U7.12 (PH0), Y1.2
unnamed: C22.1, U7.13 (PH1), Y1.1
unnamed: C35.1, C39.1, D5.1 (K), FB8.1
unnamed: C37.2, C41.2, D4.2 (A), FB2.1, U9.9 (VIN), U9.10 (EN)
unnamed: C38.1, D4.1 (K), D5.2 (A)
unnamed: C38.2, C42.1, U9.8 (C+)
unnamed: C40.1, C44.1, C45.1, C46.1, FB3.1, FB4.1, L1.2
unnamed: C42.2, C43.1, U9.5 (C-)
unnamed: C43.2, D6.2 (A)
unnamed: C50.1, C57.1, C64.1, FB4.2, U11.1 (IN), U11.2 (IN), U11.3 (EN/UV), U11.6 (PGFB)
unnamed: C51.1, C58.1, C65.1, FB5.2, U12.1 (IN), U12.2 (IN), U12.3 (IN), U12.4 (EN/UV), U12.7 (PGFB)
unnamed: C52.1, C59.1, C66.1, FB6.2, U13.1 (IN), U13.2 (IN), U13.3 (IN), U13.4 (EN/UV), U13.7 (PGFB)
unnamed: C53.1, C60.1, C67.1, FB7.2, U14.1 (IN), U14.2 (IN), U14.3 (EN/UV), U14.6 (PGFB)
unnamed: C54.1, C61.1, C68.1, FB8.2, U16.1 (IN), U16.2 (IN), U16.3 (EN/UV), U16.6 (PGFB)
unnamed: C55.1, C62.1, FB9.2, U15.1 (IN), U15.2 (IN), U15.3 (EN/UV), U15.5 (PGFB), U15.13 (IN)
unnamed: C69.1, R23.2, U11.7 (SET)
unnamed: C70.1, R25.2, U12.8 (SET)
unnamed: C71.1, R26.2, U13.8 (SET)
unnamed: C72.1, R27.2, U14.7 (SET)
unnamed: C73.1, R22.1, U15.8 (SET)
unnamed: C74.1, R28.2, U16.7 (SET)
unnamed: C102.1, R33.2, R36.1
unnamed: C103.1, R34.2, R37.1
unnamed: C104.1, R35.2, R38.1
unnamed: C110.1, C111.1, U18.18 (REGCAPD)
unnamed: C115.1, R41.2, U20.3 (CTLI)
unnamed: C117.1, U18.4 (REFOUT)
unnamed: C119.1, C121.1, U18.5 (REGCAPA)
unnamed: C122.2, C123.1, R43.1, U18.21 (AIN0)
unnamed: C123.2, C124.1, R44.1, U18.22 (AIN1)
unnamed: C125.1, U20.25 (COMP)
unnamed: C132.2, C133.1, D7.3 (K), R43.2, R50.1
unnamed: C133.2, C134.1, D8.3 (K), R44.2, R51.1
unnamed: C135.2, C136.1, C138.2, C139.1, FL1.1, L2.2, R45.2, R52.2, U20.16 (CS)
unnamed: C136.2, C137.1, C139.2, C140.1, FL1.2, L3.2, R53.2, U20.14 (OS2)
unnamed: C141.1, C142.1, C143.1, C144.1, L4.2, R60.1, U22.4 (PVIN), U22.5 (PVIN), U22.6 (VIN)
unnamed: C145.1, FL2.1, L5.2
unnamed: C145.2, FL2.2, Q3.3 (D), R62.1
unnamed: C146.1, FL2.4, U24.3 (VIN+)
unnamed: C147.1, U22.9 (SS/TR)
unnamed: C148.1, FL2.3, U24.4 (VIN-)
unnamed: C149.1, U22.13 (BOOT)
unnamed: C149.2, L6.1, U22.11 (PH), U22.12 (PH)
unnamed: C150.1, R64.2
unnamed: C151.1, R64.1, U22.8 (COMP)
unnamed: C5.2, C152.1, C172.1, C173.1, R6.2, R8.1, U4.2 (-)
unnamed: C152.2, R6.1, U4.6
unnamed: C155.1, Q4.2 (E), Q5.5 (D), Q5.6 (D), Q5.7 (D), Q5.8 (D), R68.1, U24.9 (+VDC), U24.10 (+VDC)
unnamed: C158.1, C159.1, FB10.2, U25.3 (VI)
unnamed: C162.2, U26.4 (XTAL2), Y2.3
unnamed: C163.2, U26.5 (XTAL1), Y2.1
unnamed: C164.1, C165.1, U26.6 (VDDCR)
unnamed: C174.2, R19.2
unnamed: C175.1, R67.2
unnamed: C175.2, R10.2, R11.1, TP9.1
unnamed: C178.1, C179.1, C180.1, FB2.2, L7.2
unnamed: C185.1, C186.1, C187.1, FB10.1, L9.2
unnamed: C188.1, C189.1, C190.1, C191.1, FB11.2, L10.1
unnamed: C192.1, R98.1
unnamed: D1.2 (A2), J1.1 (In), R1.1, R5.1, SW1.1
unnamed: D9.1 (A1), J5.1, L8.1, Q5.1 (S), Q5.2 (S), Q5.3 (S), Q6.2 (E)
unnamed: D10.2 (A), D11.1 (K), R12.2, R100.1
unnamed: D12.2 (A), K1.2, Q7.3 (D)
unnamed: FB12.1, J7.A4 (VBUS), J7.A9 (VBUS), J7.B4 (VBUS), J7.B9 (VBUS)
unnamed: FB12.2, R94.1, U28.5 (VBUS)
unnamed: FL3.1, J7.A7 (D-), J7.B7 (D-)
unnamed: FL3.4, J7.A6 (D+), J7.B6 (D+)
unnamed: H1.1, R105.2
unnamed: H2.1, R106.2
unnamed: J2.3, U7.82 (PD1)
unnamed: J2.4, U7.83 (PD2)
unnamed: J2.5, U7.84 (PD3)
unnamed: J2.6, U7.85 (PD4)
unnamed: J2.7, U7.86 (PD5)
unnamed: J2.8, U7.87 (PD6)
unnamed: J2.9, U7.88 (PD7)
unnamed: J3.1, U7.57 (PD10)
unnamed: J3.2, U7.58 (PD11)
unnamed: J3.3, U7.59 (PD12)
unnamed: J3.4, U7.60 (PD13)
unnamed: J3.5, U7.61 (PD14)
unnamed: J3.6, U7.62 (PD15)
unnamed: J3.7, U7.63 (PC6)
unnamed: J3.8, U7.64 (PC7)
unnamed: J3.9, U7.65 (PC8)
unnamed: J3.10, U7.66 (PC9)
unnamed: J6.1 (TD+), R88.2
unnamed: J6.2 (TD-), R87.2
unnamed: J6.3 (RD+), R86.2
unnamed: J6.6 (RD-), R85.2
unnamed: J6.11 (LLED+), R89.2
unnamed: J6.13 (RLED+), R90.2
unnamed: J7.A5 (CC1), R92.1
unnamed: J7.B5 (CC2), R93.1
unnamed: JP1.1 (A), R20.2, U7.94 (BOOT0)
unnamed: L2.1, U20.19 (LX1), U20.21 (LX1), U20.23 (LX1)
unnamed: L3.1, U20.6 (LX2), U20.8 (LX2), U20.10 (LX2)
unnamed: Q1.1 (S), Q1.2 (S), Q1.3 (S), R13.1
unnamed: Q2.3 (D), U21.2
unnamed: Q3.1 (G), R59.1, U21.3
unnamed: Q4.1 (B), Q4.3 (C), R70.1, R71.1
unnamed: Q5.4 (G), Q6.3 (C), R72.1
unnamed: Q6.1 (B), R71.2
unnamed: Q7.1 (G), R103.2, R104.2
unnamed: R1.2, R2.2, SW1.2
unnamed: R4.2, R5.2, SW1.3
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

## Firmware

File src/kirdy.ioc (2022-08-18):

#MicroXplorer Configuration settings - do not modify
ADC1.Channel-0\#ChannelRegularConversion=ADC_CHANNEL_3
ADC1.IPParameters=Rank-0\#ChannelRegularConversion,master,Channel-0\#ChannelRegularConversion,SamplingTime-0\#ChannelRegularConversion,NbrOfConversionFlag
ADC1.NbrOfConversionFlag=1
ADC1.Rank-0\#ChannelRegularConversion=1
ADC1.SamplingTime-0\#ChannelRegularConversion=ADC_SAMPLETIME_3CYCLES
ADC1.master=1
ETH.IPParameters=MediaInterface
ETH.MediaInterface=HAL_ETH_RMII_MODE
File.Version=6
GPIO.groupedBy=
KeepUserPlacement=false
Mcu.CPN=STM32F407VGT6
Mcu.Family=STM32F4
Mcu.IP0=ADC1
Mcu.IP1=DAC
Mcu.IP10=TIM4
Mcu.IP11=USB_OTG_FS
Mcu.IP2=ETH
Mcu.IP3=I2C3
Mcu.IP4=NVIC
Mcu.IP5=RCC
Mcu.IP6=SPI1
Mcu.IP7=SPI2
Mcu.IP8=SPI3
Mcu.IP9=SYS
Mcu.IPNb=12
Mcu.Name=STM32F407V(E-G)Tx
Mcu.Package=LQFP100
Mcu.Pin0=PH0-OSC_IN
Mcu.Pin1=PH1-OSC_OUT
Mcu.Pin10=PA5
Mcu.Pin11=PA6
Mcu.Pin12=PA7
Mcu.Pin13=PC4
Mcu.Pin14=PC5
Mcu.Pin15=PB0
Mcu.Pin16=PB1
Mcu.Pin17=PE8
Mcu.Pin18=PE9
Mcu.Pin19=PE10
Mcu.Pin2=PC1
Mcu.Pin20=PE11
Mcu.Pin21=PE12
Mcu.Pin22=PE13
Mcu.Pin23=PB10
Mcu.Pin24=PB11
Mcu.Pin25=PB12
Mcu.Pin26=PB13
Mcu.Pin27=PB14
Mcu.Pin28=PB15
Mcu.Pin29=PD8
Mcu.Pin3=PC2
Mcu.Pin30=PD9
Mcu.Pin31=PC9
Mcu.Pin32=PA8
Mcu.Pin33=PA9
Mcu.Pin34=PA11
Mcu.Pin35=PA12
Mcu.Pin36=PA13
Mcu.Pin37=PA14
Mcu.Pin38=PA15
Mcu.Pin39=PC10
Mcu.Pin4=PC3
Mcu.Pin40=PC11
Mcu.Pin41=PC12
Mcu.Pin42=PD0
Mcu.Pin43=PB3
Mcu.Pin44=PB4
Mcu.Pin45=PB5
Mcu.Pin46=PB6
Mcu.Pin47=PB7
Mcu.Pin48=PB8
Mcu.Pin49=VP_SYS_VS_Systick
Mcu.Pin5=PA0-WKUP
Mcu.Pin6=PA1
Mcu.Pin7=PA2
Mcu.Pin8=PA3
Mcu.Pin9=PA4
Mcu.PinsNb=50
Mcu.ThirdPartyNb=0
Mcu.UserConstants=
Mcu.UserName=STM32F407VGTx
MxCube.Version=6.5.0
MxDb.Version=DB.6.0.50
NVIC.BusFault_IRQn=true\:0\:0\:false\:false\:true\:false\:false\:false
NVIC.DebugMonitor_IRQn=true\:0\:0\:false\:false\:true\:false\:false\:false
NVIC.ForceEnableDMAVector=true
NVIC.HardFault_IRQn=true\:0\:0\:false\:false\:true\:false\:false\:false
NVIC.MemoryManagement_IRQn=true\:0\:0\:false\:false\:true\:false\:false\:false
NVIC.NonMaskableInt_IRQn=true\:0\:0\:false\:false\:true\:false\:false\:false
NVIC.PendSV_IRQn=true\:0\:0\:false\:false\:true\:false\:false\:false
NVIC.PriorityGroup=NVIC_PRIORITYGROUP_4
NVIC.SVCall_IRQn=true\:0\:0\:false\:false\:true\:false\:false\:false
NVIC.SysTick_IRQn=true\:15\:0\:false\:false\:true\:false\:true\:false
NVIC.UsageFault_IRQn=true\:0\:0\:false\:false\:true\:false\:false\:false
PA0-WKUP.GPIOParameters=GPIO_Label
PA0-WKUP.GPIO_Label=ETH_RST
PA0-WKUP.Locked=true
PA0-WKUP.Signal=GPIO_Output
PA1.Mode=RMII
PA1.Signal=ETH_REF_CLK
PA11.Mode=Device_Only
PA11.Signal=USB_OTG_FS_DM
PA12.Mode=Device_Only
PA12.Signal=USB_OTG_FS_DP
PA13.Mode=Serial_Wire
PA13.Signal=SYS_JTMS-SWDIO
PA14.Mode=Serial_Wire
PA14.Signal=SYS_JTCK-SWCLK
PA15.GPIOParameters=GPIO_Label
PA15.GPIO_Label=TADC_CS
PA15.Locked=true
PA15.Mode=NSS_Signal_Hard_Output
PA15.Signal=SPI3_NSS
PA2.Mode=RMII
PA2.Signal=ETH_MDIO
PA3.GPIOParameters=GPIO_Label
PA3.GPIO_Label=PD_MON
PA3.Locked=true
PA3.Signal=ADCx_IN3
PA4.GPIOParameters=GPIO_Label
PA4.GPIO_Label=PD_BIAS
PA4.Signal=COMP_DAC1_group
PA5.GPIOParameters=GPIO_Label
PA5.GPIO_Label=TEC_SHDN
PA5.Locked=true
PA5.Signal=GPIO_Output
PA6.GPIOParameters=GPIO_Label
PA6.GPIO_Label=TEC_VREF
PA6.Locked=true
PA6.Signal=ADCx_IN6
PA7.Mode=RMII
PA7.Signal=ETH_CRS_DV
PA8.Mode=I2C
PA8.Signal=I2C3_SCL
PA9.Mode=Activate_VBUS
PA9.Signal=USB_OTG_FS_VBUS
PB0.GPIOParameters=GPIO_Label
PB0.GPIO_Label=TEC_ISEN
PB0.Locked=true
PB0.Signal=ADCx_IN8
PB1.GPIOParameters=GPIO_Label
PB1.GPIO_Label=TEC_VSEN
PB1.Locked=true
PB1.Signal=ADCx_IN9
PB10.GPIOParameters=GPIO_Label
PB10.GPIO_Label=LDAC_CLK
PB10.Mode=TX_Only_Simplex_Unidirect_Master
PB10.Signal=SPI2_SCK
PB11.Mode=RMII
PB11.Signal=ETH_TX_EN
PB12.Mode=RMII
PB12.Signal=ETH_TXD0
PB13.Mode=RMII
PB13.Signal=ETH_TXD1
PB14.GPIOParameters=GPIO_Label
PB14.GPIO_Label=LDAC_LOAD
PB14.Locked=true
PB14.Signal=GPIO_Output
PB15.GPIOParameters=GPIO_Label
PB15.GPIO_Label=LDAC_MOSI
PB15.Locked=true
PB15.Mode=TX_Only_Simplex_Unidirect_Master
PB15.Signal=SPI2_MOSI
PB3.GPIOParameters=GPIO_Label
PB3.GPIO_Label=TDAC_CLK
PB3.Locked=true
PB3.Mode=TX_Only_Simplex_Unidirect_Master
PB3.Signal=SPI1_SCK
PB4.GPIOParameters=GPIO_Label
PB4.GPIO_Label=TDAC_SYNC
PB4.Locked=true
PB4.Signal=GPIO_Output
PB5.GPIOParameters=GPIO_Label
PB5.GPIO_Label=TDAC_MOSI
PB5.Mode=TX_Only_Simplex_Unidirect_Master
PB5.Signal=SPI1_MOSI
PB6.GPIOParameters=GPIO_Label
PB6.GPIO_Label=PWM_MAXIN
PB6.Locked=true
PB6.Signal=S_TIM4_CH1
PB7.GPIOParameters=GPIO_Label
PB7.GPIO_Label=PWM_MAXV
PB7.Locked=true
PB7.Signal=S_TIM4_CH2
PB8.GPIOParameters=GPIO_Label
PB8.GPIO_Label=PWM_MAXIP
PB8.Locked=true
PB8.Signal=S_TIM4_CH3
PC1.Mode=RMII
PC1.Signal=ETH_MDC
PC10.GPIOParameters=GPIO_Label
PC10.GPIO_Label=TADC_CLK
PC10.Mode=Full_Duplex_Master
PC10.Signal=SPI3_SCK
PC11.GPIOParameters=GPIO_Label
PC11.GPIO_Label=TADC_MISO
PC11.Mode=Full_Duplex_Master
PC11.Signal=SPI3_MISO
PC12.GPIOParameters=GPIO_Label
PC12.GPIO_Label=TADC_MOSI
PC12.Mode=Full_Duplex_Master
PC12.Signal=SPI3_MOSI
PC2.GPIOParameters=GPIO_Label
PC2.GPIO_Label=AT_EVENT
PC2.Locked=true
PC2.Signal=GPIO_Input
PC3.GPIOParameters=GPIO_Label
PC3.GPIO_Label=POE_PWR_SRC
PC3.Locked=true
PC3.Signal=GPIO_Input
PC4.Mode=RMII
PC4.Signal=ETH_RXD0
PC5.Mode=RMII
PC5.Signal=ETH_RXD1
PC9.Mode=I2C
PC9.Signal=I2C3_SDA
PD0.GPIOParameters=GPIO_Label
PD0.GPIO_Label=TADC_SYNC
PD0.Locked=true
PD0.Signal=GPIO_Output
PD8.GPIOParameters=GPIO_Label
PD8.GPIO_Label=LDAC_CS
PD8.Locked=true
PD8.Signal=GPIO_Output
PD9.GPIOParameters=GPIO_Label
PD9.GPIO_Label=LD_EN
PD9.Locked=true
PD9.Signal=GPIO_Output
PE10.GPIOParameters=GPIO_Label
PE10.GPIO_Label=REV2
PE10.Locked=true
PE10.Signal=GPIO_Input
PE11.GPIOParameters=GPIO_Label
PE11.GPIO_Label=REV3
PE11.Locked=true
PE11.Signal=GPIO_Input
PE12.GPIOParameters=GPIO_Label
PE12.GPIO_Label=REV4
PE12.Locked=true
PE12.Signal=GPIO_Input
PE13.GPIOParameters=GPIO_Label
PE13.GPIO_Label=REV5
PE13.Locked=true
PE13.Signal=GPIO_Input
PE8.GPIOParameters=GPIO_Label
PE8.GPIO_Label=REV0
PE8.Locked=true
PE8.Signal=GPIO_Input
PE9.GPIOParameters=GPIO_Label
PE9.GPIO_Label=REV1
PE9.Locked=true
PE9.Signal=GPIO_Input
PH0-OSC_IN.Mode=HSE-External-Oscillator
PH0-OSC_IN.Signal=RCC_OSC_IN
PH1-OSC_OUT.Mode=HSE-External-Oscillator
PH1-OSC_OUT.Signal=RCC_OSC_OUT
PinOutPanel.RotationAngle=0
ProjectManager.AskForMigrate=true
ProjectManager.BackupPrevious=false
ProjectManager.CompilerOptimize=6
ProjectManager.ComputerToolchain=false
ProjectManager.CoupleFile=false
ProjectManager.CustomerFirmwarePackage=
ProjectManager.DefaultFWLocation=true
ProjectManager.DeletePrevious=true
ProjectManager.DeviceId=STM32F407VGTx
ProjectManager.FirmwarePackage=STM32Cube FW_F4 V1.27.0
ProjectManager.FreePins=false
ProjectManager.HalAssertFull=false
ProjectManager.HeapSize=0x200
ProjectManager.KeepUserCode=true
ProjectManager.LastFirmware=true
ProjectManager.LibraryCopy=0
ProjectManager.MainLocation=Core/Src
ProjectManager.NoMain=false
ProjectManager.PreviousToolchain=
ProjectManager.ProjectBuild=false
ProjectManager.ProjectFileName=kirdy.ioc
ProjectManager.ProjectName=kirdy
ProjectManager.RegisterCallBack=
ProjectManager.StackSize=0x400
ProjectManager.TargetToolchain=EWARM V8.50
ProjectManager.ToolChainLocation=
ProjectManager.UnderRoot=false
ProjectManager.functionlistsort=1-SystemClock_Config-RCC-false-HAL-false,2-MX_GPIO_Init-GPIO-false-HAL-true,3-MX_ADC1_Init-ADC1-false-HAL-true,4-MX_DAC_Init-DAC-false-HAL-true,5-MX_ETH_Init-ETH-false-HAL-true,6-MX_I2C3_Init-I2C3-false-HAL-true,7-MX_SPI1_Init-SPI1-false-HAL-true,8-MX_SPI2_Init-SPI2-false-HAL-true,9-MX_SPI3_Init-SPI3-false-HAL-true,10-MX_TIM4_Init-TIM4-false-HAL-true,11-MX_USB_OTG_FS_PCD_Init-USB_OTG_FS-false-HAL-true
RCC.48MHZClocksFreq_Value=48000000
RCC.AHBFreq_Value=168000000
RCC.APB1CLKDivider=RCC_HCLK_DIV4
RCC.APB1Freq_Value=42000000
RCC.APB1TimFreq_Value=84000000
RCC.APB2CLKDivider=RCC_HCLK_DIV2
RCC.APB2Freq_Value=84000000
RCC.APB2TimFreq_Value=168000000
RCC.CortexFreq_Value=168000000
RCC.EthernetFreq_Value=168000000
RCC.FCLKCortexFreq_Value=168000000
RCC.FamilyName=M
RCC.HCLKFreq_Value=168000000
RCC.HSE_VALUE=25000000
RCC.HSI_VALUE=16000000
RCC.I2SClocksFreq_Value=96000000
RCC.IPParameters=48MHZClocksFreq_Value,AHBFreq_Value,APB1CLKDivider,APB1Freq_Value,APB1TimFreq_Value,APB2CLKDivider,APB2Freq_Value,APB2TimFreq_Value,CortexFreq_Value,EthernetFreq_Value,FCLKCortexFreq_Value,FamilyName,HCLKFreq_Value,HSE_VALUE,HSI_VALUE,I2SClocksFreq_Value,LSE_VALUE,LSI_VALUE,MCO2PinFreq_Value,PLLCLKFreq_Value,PLLM,PLLN,PLLQ,PLLQCLKFreq_Value,RTCFreq_Value,RTCHSEDivFreq_Value,SYSCLKFreq_VALUE,SYSCLKSource,VCOI2SOutputFreq_Value,VCOInputFreq_Value,VCOOutputFreq_Value,VcooutputI2S
RCC.LSE_VALUE=32768
RCC.LSI_VALUE=32000
RCC.MCO2PinFreq_Value=168000000
RCC.PLLCLKFreq_Value=168000000
RCC.PLLM=25
RCC.PLLN=336
RCC.PLLQ=7
RCC.PLLQCLKFreq_Value=48000000
RCC.RTCFreq_Value=32000
RCC.RTCHSEDivFreq_Value=12500000
RCC.SYSCLKFreq_VALUE=168000000
RCC.SYSCLKSource=RCC_SYSCLKSOURCE_PLLCLK
RCC.VCOI2SOutputFreq_Value=192000000
RCC.VCOInputFreq_Value=1000000
RCC.VCOOutputFreq_Value=336000000
RCC.VcooutputI2S=96000000
SH.ADCx_IN3.0=ADC1_IN3,IN3
SH.ADCx_IN3.ConfNb=1
SH.ADCx_IN6.0=ADC1_IN6,IN6
SH.ADCx_IN6.ConfNb=1
SH.ADCx_IN8.0=ADC1_IN8,IN8
SH.ADCx_IN8.ConfNb=1
SH.ADCx_IN9.0=ADC1_IN9,IN9
SH.ADCx_IN9.ConfNb=1
SH.COMP_DAC1_group.0=DAC_OUT1,DAC_OUT1
SH.COMP_DAC1_group.ConfNb=1
SH.S_TIM4_CH1.0=TIM4_CH1,PWM Generation1 CH1
SH.S_TIM4_CH1.ConfNb=1
SH.S_TIM4_CH2.0=TIM4_CH2,PWM Generation2 CH2
SH.S_TIM4_CH2.ConfNb=1
SH.S_TIM4_CH3.0=TIM4_CH3,PWM Generation3 CH3
SH.S_TIM4_CH3.ConfNb=1
SPI1.CalculateBaudRate=42.0 MBits/s
SPI1.Direction=SPI_DIRECTION_2LINES
SPI1.IPParameters=VirtualType,Mode,Direction,CalculateBaudRate
SPI1.Mode=SPI_MODE_MASTER
SPI1.VirtualType=VM_MASTER
SPI2.CalculateBaudRate=21.0 MBits/s
SPI2.Direction=SPI_DIRECTION_2LINES
SPI2.IPParameters=VirtualType,Mode,Direction,CalculateBaudRate
SPI2.Mode=SPI_MODE_MASTER
SPI2.VirtualType=VM_MASTER
SPI3.CalculateBaudRate=21.0 MBits/s
SPI3.Direction=SPI_DIRECTION_2LINES
SPI3.IPParameters=VirtualType,Mode,Direction,CalculateBaudRate,VirtualNSS
SPI3.Mode=SPI_MODE_MASTER
SPI3.VirtualNSS=VM_NSSHARD
SPI3.VirtualType=VM_MASTER
TIM4.Channel-PWM\ Generation1\ CH1=TIM_CHANNEL_1
TIM4.Channel-PWM\ Generation2\ CH2=TIM_CHANNEL_2
TIM4.Channel-PWM\ Generation3\ CH3=TIM_CHANNEL_3
TIM4.IPParameters=Channel-PWM Generation1 CH1,Channel-PWM Generation2 CH2,Channel-PWM Generation3 CH3
USB_OTG_FS.IPParameters=VirtualMode
USB_OTG_FS.VirtualMode=Device_Only
VP_SYS_VS_Systick.Mode=SysTick
VP_SYS_VS_Systick.Signal=SYS_VS_Systick
board=custom

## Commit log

2022-06-12 add project
    [kirdy.kicad_pcb, kirdy.kicad_sch]
2022-06-12 add symbol and footprint lib
    [kirdy.kicad_sch]
2022-06-13 add driver stage sch
    [driveStage.kicad_sch, kirdy.kicad_sch]
2022-06-13 minor improvements
    [driveStage.kicad_sch, kirdy.kicad_sch]
2022-06-13 add ref dac
    [driveStage.kicad_sch, kirdy.kicad_sch, refdac.kicad_sch]
2022-06-14 finish drive stage, add sheets
    [driveStage.kicad_sch, kirdy.kicad_sch, mcu.kicad_sch, refdac.kicad_sch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]
2022-06-15 remove ref dac sheet, finish thermostat
    [driveStage.kicad_sch, kirdy.kicad_sch, refdac.kicad_sch, thermostat.kicad_sch]
2022-06-15 add TEC V sense, filter TEC I sense
    [driveStage.kicad_sch, kirdy.kicad_sch, thermostat.kicad_sch]
2022-06-16 before beer
    [asupply.kicad_sch, driveStage.kicad_sch, kirdy.kicad_sch, photodiode.kicad_sch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]
2022-06-16 analog supply complete
    [asupply.kicad_sch, kirdy.kicad_sch]
2022-07-02 add PoE
    [asupply.kicad_sch, driveStage.kicad_sch, dsupply.kicad_sch, kirdy.kicad_sch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]
2022-07-02 complete digital supply
    [dsupply.kicad_sch, kirdy.kicad_sch]
2022-07-02 add ethernet
    [driveStage.kicad_sch, dsupply.kicad_sch, eth.kicad_sch, kirdy.kicad_sch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]
2022-07-03 add USB
    [asupply.kicad_sch, driveStage.kicad_sch, dsupply.kicad_sch, eth.kicad_sch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]
2022-07-03 add MCU basic connections
    [driveStage.kicad_sch, dsupply.kicad_sch, eth.kicad_sch, kirdy.kicad_sch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]
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2022-07-03 complete mcu
    [asupply.kicad_sch, driveStage.kicad_sch, dsupply.kicad_sch, eth.kicad_sch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]
2022-07-04 first draft complete
    [asupply.kicad_sch, driveStage.kicad_sch, dsupply.kicad_sch, eth.kicad_sch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]
2022-07-04 Complete BOM, FP assignment
    [asupply.kicad_sch, driveStage.kicad_sch, dsupply.kicad_sch, eth.kicad_sch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]
2022-07-04 rough placement
    [driveStage.kicad_sch, kirdy.kicad_pcb, kirdy.kicad_sch]
2022-07-04 add bom, finish rough placement
    [driveStage.kicad_sch, kirdy.csv, kirdy.kicad_pcb, kirdy.kicad_sch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]
2022-07-05 complete placement
    [asupply.kicad_sch, driveStage.kicad_sch, kirdy.kicad_pcb, kirdy.kicad_sch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]
2022-07-06 routing, bom update
    [eth.kicad_sch, kirdy.csv, kirdy.kicad_pcb, kirdy.kicad_sch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]
2022-07-06 more routing
    [asupply.kicad_sch, driveStage.kicad_sch, dsupply.kicad_sch, eth.kicad_sch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]
2022-07-06 roughly done
    [kirdy.kicad_pcb]
2022-07-06 passes DRC
    [kirdy.kicad_pcb]
2022-08-04 add V01 production files, bug fixes
    [Marking.dxf, asupply.kicad_sch, driveStage.kicad_sch, dsupply.kicad_sch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]
2022-08-18 v 0.2 schematics
    [asupply.kicad_sch, driveStage.kicad_sch, dsupply.kicad_sch, eth.kicad_sch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]
2022-08-19 add gate pull down
    [driveStage.kicad_sch, kirdy.kicad_sch]
2022-08-20 remove rev resistors
    [kirdy.kicad_sch, mcu.kicad_sch]
2022-08-20 change damper
    [asupply.kicad_sch, driveStage.kicad_sch, dsupply.kicad_sch, eth.kicad_sch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]
2022-08-20 change PD LD circuit
    [asupply.kicad_sch, driveStage.kicad_sch, dsupply.kicad_sch, kirdy.kicad_sch]
2022-08-20 change diodes
    [asupply.kicad_sch, driveStage.kicad_sch, kirdy.kicad_sch]
2022-08-22 change LD shorting circuit
    [driveStage.kicad_sch, kirdy.kicad_sch, mcu.kicad_sch, thermostat.kicad_sch]
2022-08-25 v2 schematics, fp assignment
    [driveStage.kicad_sch, dsupply.kicad_sch, kirdy.kicad_sch, mcu.kicad_sch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]
2022-08-25 import sch to pcb
    [asupply.kicad_sch, dsupply.kicad_sch, eth.kicad_sch, kirdy.kicad_sch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]
2022-09-03 fix eth
    [eth.kicad_sch, kirdy.kicad_pcb, kirdy.kicad_sch]
2022-09-04 placement v2
    [asupply.kicad_sch, driveStage.kicad_sch, eth.kicad_sch, kirdy.kicad_pcb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]
2022-09-04 update palcement
    [kirdy.kicad_pcb, kirdy.kicad_sch, thermostat.kicad_sch]
2022-09-05 some layout
    [kirdy.kicad_pcb, mcu.kicad_sch, usb.kicad_sch]
2022-09-07 finish v2 layout
    [driveStage.kicad_sch, kirdy.kicad_sch, thermostat.kicad_sch]
2022-09-09 improve relay power circuitry
    [asupply.kicad_sch, driveStage.kicad_sch, dsupply.kicad_sch, kirdy-B_Cu.gbl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]
2023-10-12 Mirgrate to kicad7
    [asupply.kicad_sch, driveStage.kicad_sch, dsupply.kicad_sch, eth.kicad_sch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]
2023-10-12 sch: R13 Power Resistor change to PDY10R000F
    [driveStage.kicad_sch]
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2023-10-25 sch: Add soft start to 12V PWR Jack input
    [dsupply.kicad_sch]
2023-10-25 sch: Fix Issue #15
    [asupply.kicad_sch]
2023-10-25 sch: Modify dsupply freq_comp network - See Issue #21
    [dsupply.kicad_sch]
2023-10-25 sch: Add REF3033 for MCU ADC VREF
    [mcu.kicad_sch]
2023-10-25 sch: Use TL082 for PD_Mon TIA and LPF Stage
    [driveStage.kicad_sch]
2023-10-25 sch: LD DAC add parallel Cap to output resistor - Increase the Mod_In Signal Bandwidth - See Issue #22
    [driveStage.kicad_sch]
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2023-10-25 sch: Tune the LD V-I Output Stage Feedback Network - R67 -> 0R - C175 -> 100pF
    [driveStage.kicad_sch]
2023-10-25 sch: Tune LD- Out Series RC Network - R98 3R3 -> 10R - C192 100n PPS -> DNP - Add C199 2n2 in parallel C192
    [driveStage.kicad_sch]
2023-10-25 sch: correct ethernet phy sigs connections to ESD - Pull up eth signals with 100R instead of pull down
    [eth.kicad_sch]
2023-10-25 sch: Fix Issue #14
    [asupply.kicad_sch]
2023-10-25 sch: Do not pass MCU RST to ETH - D3 -> DNP
    [mcu.kicad_sch]
2023-10-25 sch: Support Temp ADC in alternate footprint - Issue #12 - Add Alternate AD7172-4BCPZ circuitry, symbol, footprint and 3D model
    [thermostat.kicad_sch]
2023-10-25 sch: Set DNP for DNP components
    [driveStage.kicad_sch, eth.kicad_sch]
2023-10-27 sch: Change PoE RJ45 Jack and change PM1202 Symbol - Use the same PoE RJ45 as sinara-hw thermostat - Add PM1202 Power input pins (VB+, VB-) - Remove PoE softstart circuit as PM1202 has inrush current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
    [dsupply.kicad_sch, eth.kicad_sch, kirdy.kicad_sch, mcu.kicad_sch]
2023-10-27 sch: Correct SWD Header MF/PN and Update Footprint - Use Adafuit 4048 Mini SWD Headers - Silkscreen is modified to indicate orientation of the header
    [mcu.kicad_sch]
2023-10-27 sch: Add redundant 2.54mm SWD Header
    [mcu.kicad_sch]
2023-10-30 sch: Correct typos in TEC_~{SHDN} ports
    [kirdy.kicad_sch, mcu.kicad_sch]
2023-10-30 sch: add lpf at TEC_VSEN Buffer Output
    [thermostat.kicad_sch]
2023-10-30 sch: fix Temperature ADC SPI Connections - Fix Issue #25
    [kirdy.kicad_sch]
2023-10-30 symbol: AD7172-4 sets DNC pin to unconnected type
    [thermostat.kicad_sch]
2023-10-31 symbol: correct RJ45 VC output pin type - from power input to power output
    [eth.kicad_sch]
2023-10-31 sch: correct POE_VC* pins name case - PoE_VC* -> POE_VC*
    [eth.kicad_sch, kirdy.kicad_sch]
2023-10-31 sch: Update power related flags and nets symbols - Update the symbol from the kicad 7 built-in library - Remove ERC warnings
    [asupply.kicad_sch, driveStage.kicad_sch, dsupply.kicad_sch, eth.kicad_sch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]
2023-10-31 footprint: Add TL082Hx TI SOIC-8 footprint
    [driveStage.kicad_sch]
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2023-11-08 thermostat: Fix wrong P/N in TEC Current Sense Res - Fix Issue #26
    [thermostat.kicad_sch]
2023-11-08 sch: Fix incorrect TEC polarity in thermostat - Fix Issue #27
    [thermostat.kicad_sch]
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2023-11-10 sch: Update Title Block Info - rev0.3 -> rev0_3 - Correct the title of each schematics - Update the modified time
    [asupply.kicad_sch, driveStage.kicad_sch, dsupply.kicad_sch, eth.kicad_sch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]
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2023-11-10 sch, pcb: Correct MFR/PN and optimize BOM
    [asupply.kicad_sch, driveStage.kicad_sch, dsupply.kicad_sch, eth.kicad_sch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]
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2023-11-27 sch, pcb: Replace FB of -6V +15V LDO with inductor - Build a Pi LPF on the input side
    [asupply.kicad_sch]
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2023-11-27 sch, pcb: Remove X7R, X5R at input LT304x - Reduce the number of Tantalum Capacitor Used - Replace some non critical ones with Electrolytic Caps
    [asupply.kicad_sch, driveStage.kicad_sch, dsupply.kicad_sch, eth.kicad_sch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]
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2023-11-29 sch, pcb: Add TAN Caps to all LT304x SET Pin - Prevent noise due to microphonics to be amplified by internal Amp - Remove the input TAN Caps as LT304x PSRR is very good - Replace TAN Caps in the 12V 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
    [asupply.kicad_sch, dsupply.kicad_sch, eth.kicad_sch]
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2023-11-30 sch: Correct Front Panel Kit MRF/PN & Value typo
    [kirdy.kicad_sch]
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2023-12-13 sch, pcb: correct polarity of LT3094xMSE C_Set
    [asupply.kicad_sch]
2023-12-13 Correct graphical mistakes in LTC3261 symbol - no functional changes
    [asupply.kicad_sch]
2023-12-13 PCB: Correct Y169010R0000T9L Footprint - Add more space between the pin holes and resistor body
    [driveStage.kicad_sch]
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2023-12-19 sch, pcb: Correct opamp input polarity of TEC_VSEN - +ve IN connects to TEC+ - -ve IN connects to TEC-
    [thermostat.kicad_sch]
2024-01-24 sch: correct MFR/PNs for BSS138, TLV9001, TPS54620
    [driveStage.kicad_sch, dsupply.kicad_sch, thermostat.kicad_sch]
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2025-06-24 Fix issiues from lis, see bug/issiue list in DOC directory
    [asupply.kicad_sch, driveStage.kicad_sch, dsupply.kicad_sch, eth.kicad_sch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]
